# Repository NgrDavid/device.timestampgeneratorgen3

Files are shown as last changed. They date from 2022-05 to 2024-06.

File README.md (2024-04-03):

## Harp Timestamp Generator Gen3

This device generates programable timestamps to up to 6 harp devices.

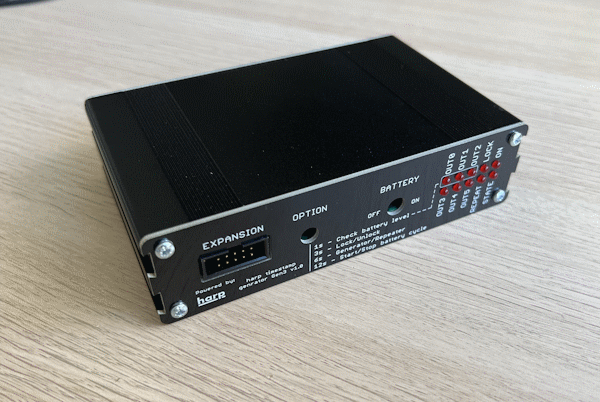
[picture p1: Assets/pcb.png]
HarpTimestampGeneratorGen3


### Key Features ###

* TBA

### Connectivity ###

* TBA

## Interface ##

The interface with the Harp Output Expander can be done through [Bonsai](https://bonsai-rx.org/).

## Licensing ##

Each subdirectory will contain a license or, possibly, a set of licenses if it involves both hardware and software.

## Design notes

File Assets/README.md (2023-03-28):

### Licensing
Copyright Filipe Carvalho 2021

<br />This work is licensed under a <a rel="license" href="http://creativecommons.org/licenses/by/4.0/">Creative Commons Attribution 4.0 International License</a>.

#### You are free to:
*Share* — copy and redistribute the material in any medium or format.

*Adapt* — remix, transform, and build upon the material for any purpose, even commercially.

#### Under the following terms:
*Attribution* — You must give appropriate credit, provide a link to the license, and indicate if changes were made. You may do so in any reasonable manner, but not in any way that suggests the licensor endorses you or your use.

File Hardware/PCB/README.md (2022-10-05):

# Harp Timestamp Generator Gen1

## Licensing

The designs, documentation, and photos available in this repository are free: you can redistribute it and/or modify it under the terms of the used license.
Check file named LICENSE.

Copyright OEPS 2021-2022

<br />This work is licensed under a <a rel="license" href="http://creativecommons.org/licenses/by-nc-sa/3.0/igo/">Creative Commons Attribution-NonCommercial-ShareAlike 3.0 IGO License</a>.

If your are interested in obtaining a license to sell this device, please contact info@oeps.tech

[1]: https://docs.google.com/spreadsheets/d/1aobmmEzBDethzIlrm1eg0eYkBqlyX3s9WbA9KgRwVQI/edit?usp=sharing

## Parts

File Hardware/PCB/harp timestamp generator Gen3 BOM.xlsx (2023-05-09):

Qty | Value | Package | Parts | MPN | Type
ASSEMBLY HOUSE
1 | CFPA | CFPA | BUTTON | CFPA-1FB4-A2T | SMD
30 | 100nF | C0402 | C1, C3, C5, C7, C9, C12, C13, C14, C15, C16, C17, C18, C19, C20, C21, C22, C25, C26, C27, C28, C30, C31, C32, C35, C36, C37, C38, C41, C42, C62 | CGA2B3X7R1H104K050BB | SMD
5 | 4.7uF | C0603 | C8, C10, C11, C23, C24 | C1608X6S1C475K080AC | SMD
1 | 4.7nF | C0402 | C2 | 885012205084 | SMD
1 | 330nF | C0402 | C29 | GRM155R61A334KE15D | SMD
2 | 10nF | C0402 | C33, C34 | GCM155R71E103KA37D | SMD
2 | 47pF | C0402 | C4, C6 | 04025A470JAT2A | SMD
1 | 100u 25V | TT2D6 | C39 | EEU-FM1E101B | TH
1 | 330pF | C0402 | C40 | C0402C331J5GAC7867 | SMD
7 | CLCK_JACK | 35RASMT2BHNTRX | CLKIN, CLKOUT0, CLKOUT1, CLKOUT2, CLKOUT3, CLKOUT4, CLKOUT5 | 35RASMT2BHNTRX | SMD
1 | 330 Ohms @ 100MHz | R0603 | F1 | BLM18SG331TN1D | SMD
2 | DNI | DNI | D1, D2 | DNI | DNI
1 | MCP73831T-2ATI/OT | TSOT23-5 | IC1 | MCP73831T-2ATI/OT | SMD
3 | SN74LVC1G125DBVT | SOT23-5 | IC10, IC18, IC19 | SN74LVC1G125DBVT | SMD
6 | SI8621BC-B-IS | SOIC8 | IC12, IC13, IC14, IC15, IC16, IC17 | SI8621BC-B-ISR | SMD | Replacements: SI8621BB-B-IS
1 | USBLC6-2SC6 | SOT23-6L | IC2 | USBLC6-2SC6 | SMD
1 | FT232RL | SSOP28 | IC3 | FT232RL-REEL | SMD
1 | TPS2114 | TSSOP8 | IC4 | TPS2114APWR | SMD
2 | TLV70033DDCR | TSOT23-5 | IC5, IC11 | LP5951MFX-3.3/NOPB | SMD
1 | ATXMEGA16A4U-AU | QFP80P1200X1200X120-44N | IC6 | ATXMEGA16A4U-A | SMD
3 | M74VHC1GT126DF1G | SC70-5 | IC7, IC8, IC9 | M74VHC1GT126DF1G | SMD
1 | 40R@100MHz | R0805 | L1 | MI0805K400R-10 | SMD
5 | 569-0112-100 | 569-011X-X00_LED_ARRAY | LED1, LED2, LED3, LED4, LED5 | 569-0111-100F | TH
1 | OSCILLATOR | OSCILLATOR_3.2X2.5 | OSC1 | O 32,0-JT32C-A-K-3,3-LF | SMD
1 | 2x3_header | MA03-2 | PDI | 67996-206HLF | TH
1 | RTU002P02T106 | SOT323 | Q1 | RTU002P02T106 | SMD
1 | BC817-40W | SOT323-BEC | Q2 | BC817-40W,135 | SMD
1 | BC817-40LT1SMD | SOT23-BEC | Q3 | SBC817-40LT1G | SMD
1 | DMG1012UW | SOT323 | Q4 | DMG1012UW-7 | SMD
1 | DMP2035U-7 | SOT323 | Q5 | PMF170XP,115 | SMD
1 | 1M | R0402 | R1 | CRCW04021M00FKED | SMD
3 | 100R | R0603 | R10, R11, R12 | CRCW0603100RFKEAHP | SMD
3 | 4k5 | R0402 | R13, R17, R19 | RT0402BRD074K53L | SMD
1 | 20R | R2512 | R15 | CRM2512-FX-20R0ELF | SMD
1 | 10R | R0402 | R2 | ERJ-PA2J100X | SMD
1 | 0R | R0402 | R20 | RC0402JR-070RL | SMD
1 | DNI | R0402 | R26 | DNI | DNI
12 | 1k | R0402 | R14, R21, R22, R23, R24, R25, R27, R28, R29, R30, R31, R_I_MAX | CRCW04021K00FKED | SMD
8 | 10k | R0402 | R3, R7, R9, R16, R18, R50, R54, R55 | CRCW040210K0FKED | SMD
10 | 330R | R0402 | R33, R34, R35, R36, R37, R40, R41, R42, R44, R45 | RC0402FR-07330RL | SMD
1 | 51k 0.1% | R0402 | R4 | ERA-2AEB513X | SMD
2 | 14k7 0.1% | R0402 | R5, R6 | RT0402BRD0714K7L | SMD
1 | 100k | R0402 | R48 | ERJ-2RKF1003X | SMD
1 | I/O Header | ML10L | SV1 | SBH11-PBPC-D05-RA-BK | TH
10 | BC850 | SOT23 | T1, T2, T3, T4, T5, T6, T7, T8, T9, T10 | BC850C,215 | SMD
1 | mini USB | 240-0002-1 | USB | UX60-MB-5S8 | SMD
1 | Switch SPDT | 7101MD9ABE | BATEN | 7101MD9ABE | TH
1 | B2B-PH-K-S(LF)(SN) | JST-XH-02-PACKAGE-ROUND-PAD | X1 | B2B-XH-A(LF)(SN) | TH
POST-PRODUCTION
1 |  |  | Front Panel PCB | PCBWAY
1 |  |  | Rear Panel PCB | PCBWAY
1 |  |  | Enclosure | B5-080BK
1 |  |  | Battery lithium Polymer 2 Ah | MIKROE-1120 | -
4 |  |  | Bumper Cylindrical Dome 9.53mm | SJ-5306-CLEAR-3000/CASE
ACCESSORIES
3 |  |  | 3.5mm stereo jack cable 0.3 m, Black | P312-001 | -
4 |  |  | 3.5mm stereo jack cable 1.2 m, Black | AV13646
1 |  |  | 0.9 left angle USB cable | USB2HABM3RA
NOTES
 |  |  |  | Number of unique parts | 48
 |  |  |  | Number of SMD unique parts | 42
 |  |  |  | Number of SMD parts | 135
 |  |  |  | Number of TH unique parts | 6
 |  |  |  | Number of TH parts | 10

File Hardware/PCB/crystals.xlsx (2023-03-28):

Digikey PN | MNF PN | @25C [ppm] | Range of temperatures [ppm] | Supply Change [ppm] | Load Change [ppm] | Aging/year [ppm] |  | Dimensions [mm] | Pinout | Current [mA] | Type
XC2259CT-ND | ECS-TXO-2520-33-320-AN-TR | 2 | 2.5 | 0.2 | 0.2 | 1 | 5.9 | 2.5 x 2.0 | En/Dis, GND, OUT, VDD | 6 | HCMOS TXCO
1908-1044-1-ND | O 32,0-JT32C-A-K-3,3-LF | 0.5 | 2.5 | 0.2 | 0.2 | 1 | 4.4 | 3.2 x 2.5 | En/Dis, GND, OUT, VDD | 4.8 | HCMOS TXCO
50-ECS-TXO-2520MV-320-AN-CT-ND | ECS-TXO-2520MV-320-AN-TR | 1.5 | 2.5 | 0.3 | 0.3 | 1 | 5.6 | 2.5 x 2.0 | En/Dis, GND, OUT, VDD | 6 | CMOS TXCO
50-ECS-TXO-2520MV-320-AY-CT-ND | ECS-TXO-2520MV-320-AY-TR | 1.5 | 2.5 | 0.3 | 0.3 | 1 | 5.6 | 2.5 x 2.0 | En/Dis, GND, OUT, VDD | 6 | CMOS TXCO
50-ECS-TXO-25CSMV-320-BM-CT-ND | ECS-TXO-25CSMV-320-BM-TR | 2 | 1 | 0.2 | 0.2 | 1 | 4.4 | 2.5 x 2.0 | GND, GND, OUT, VDD | 2.5 | Clipped Sinewave TSCO

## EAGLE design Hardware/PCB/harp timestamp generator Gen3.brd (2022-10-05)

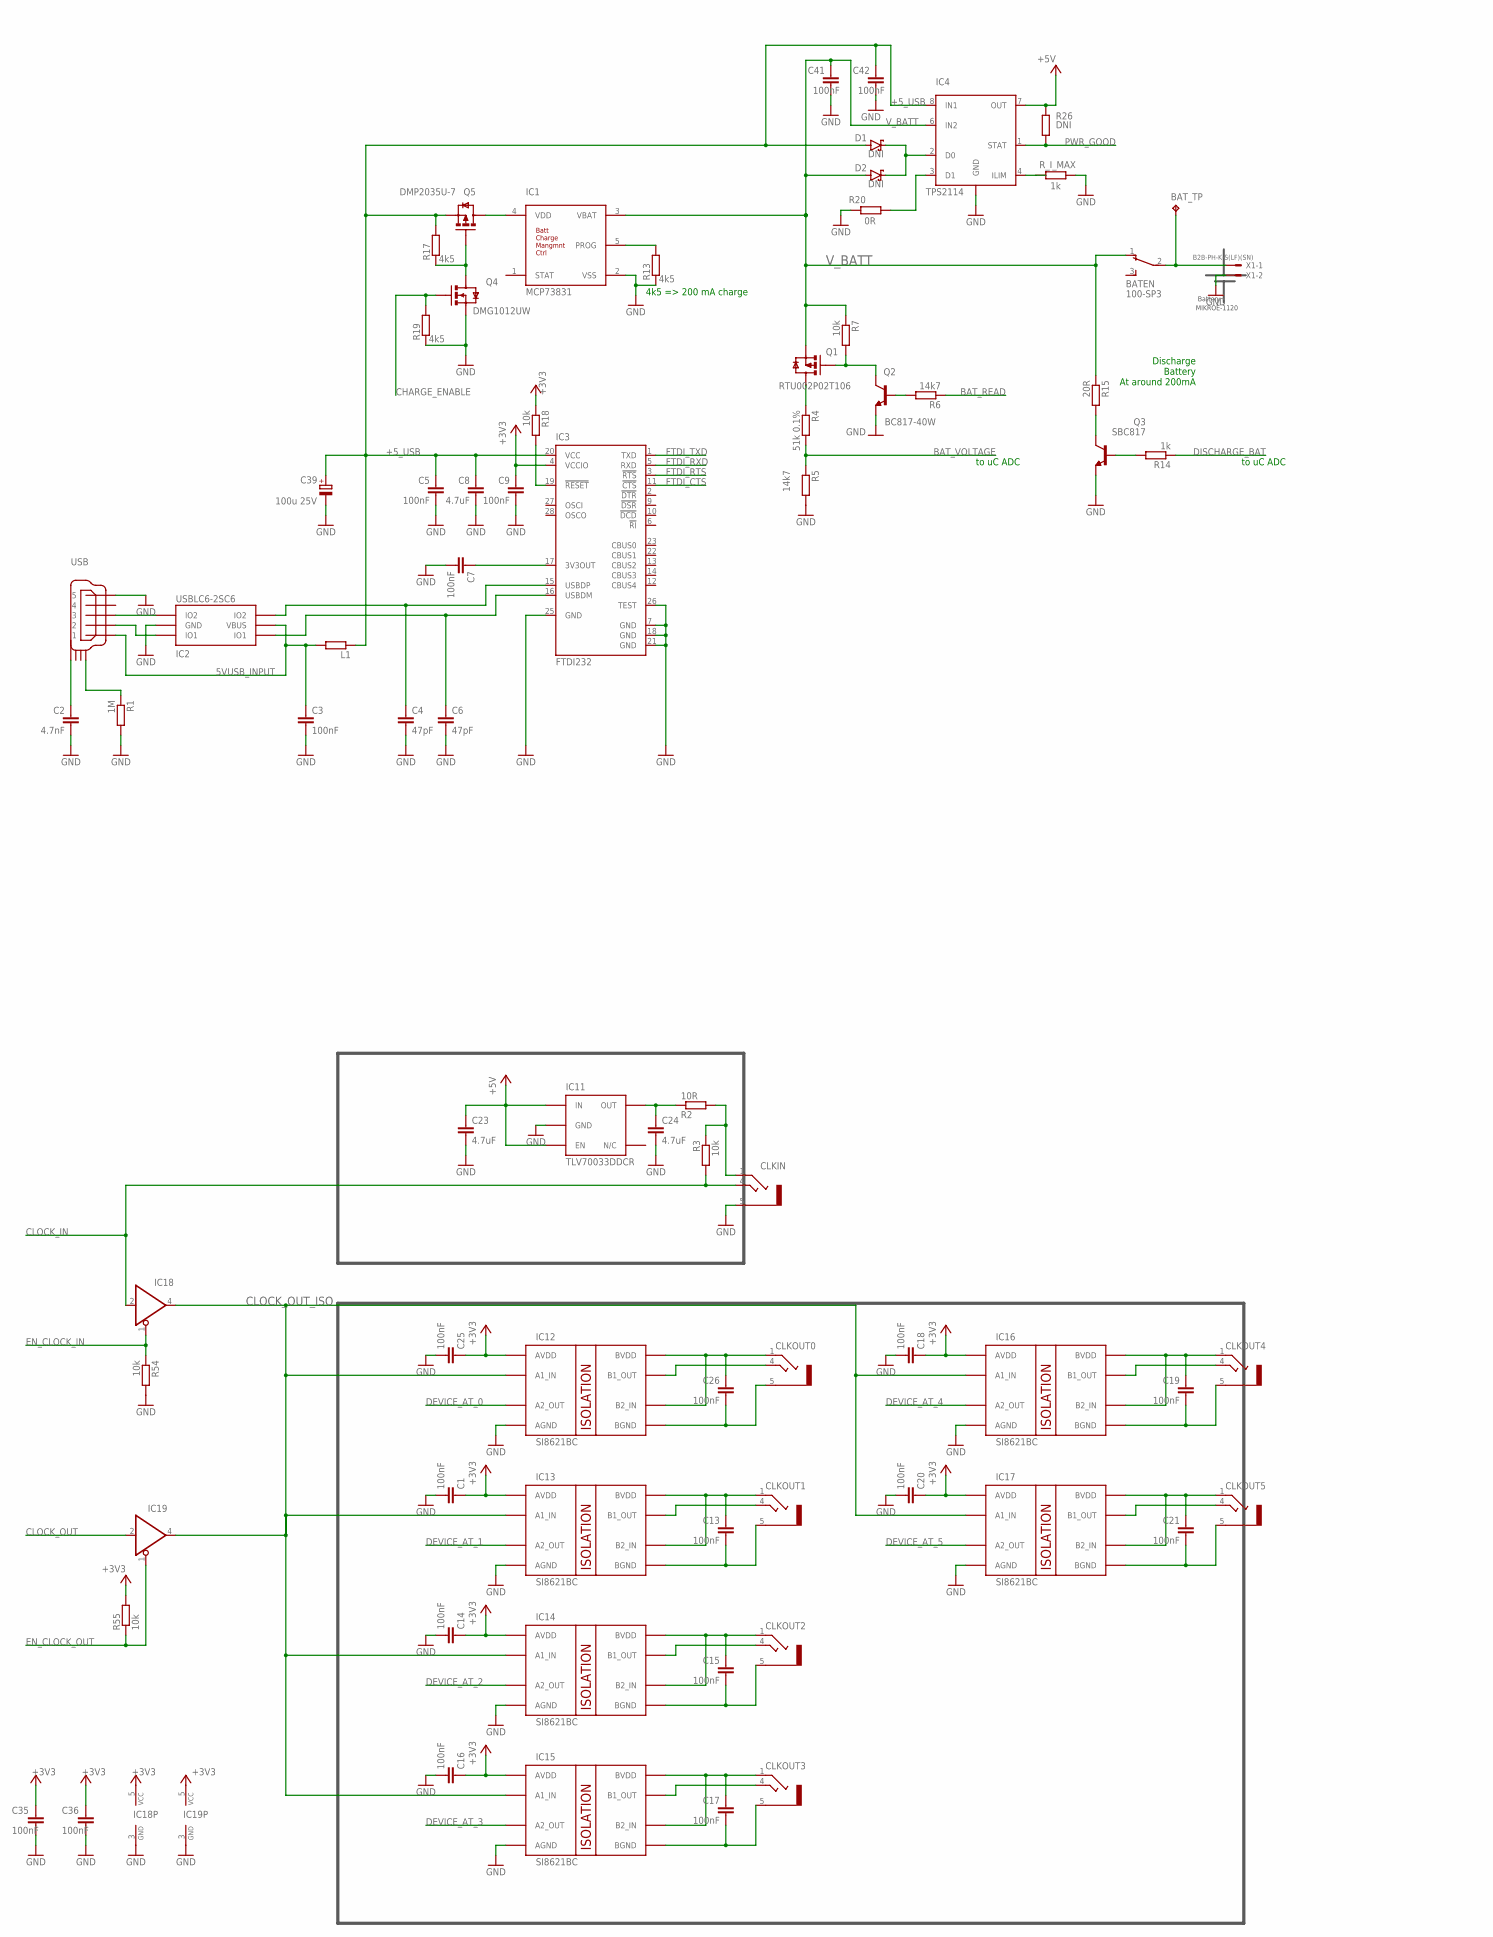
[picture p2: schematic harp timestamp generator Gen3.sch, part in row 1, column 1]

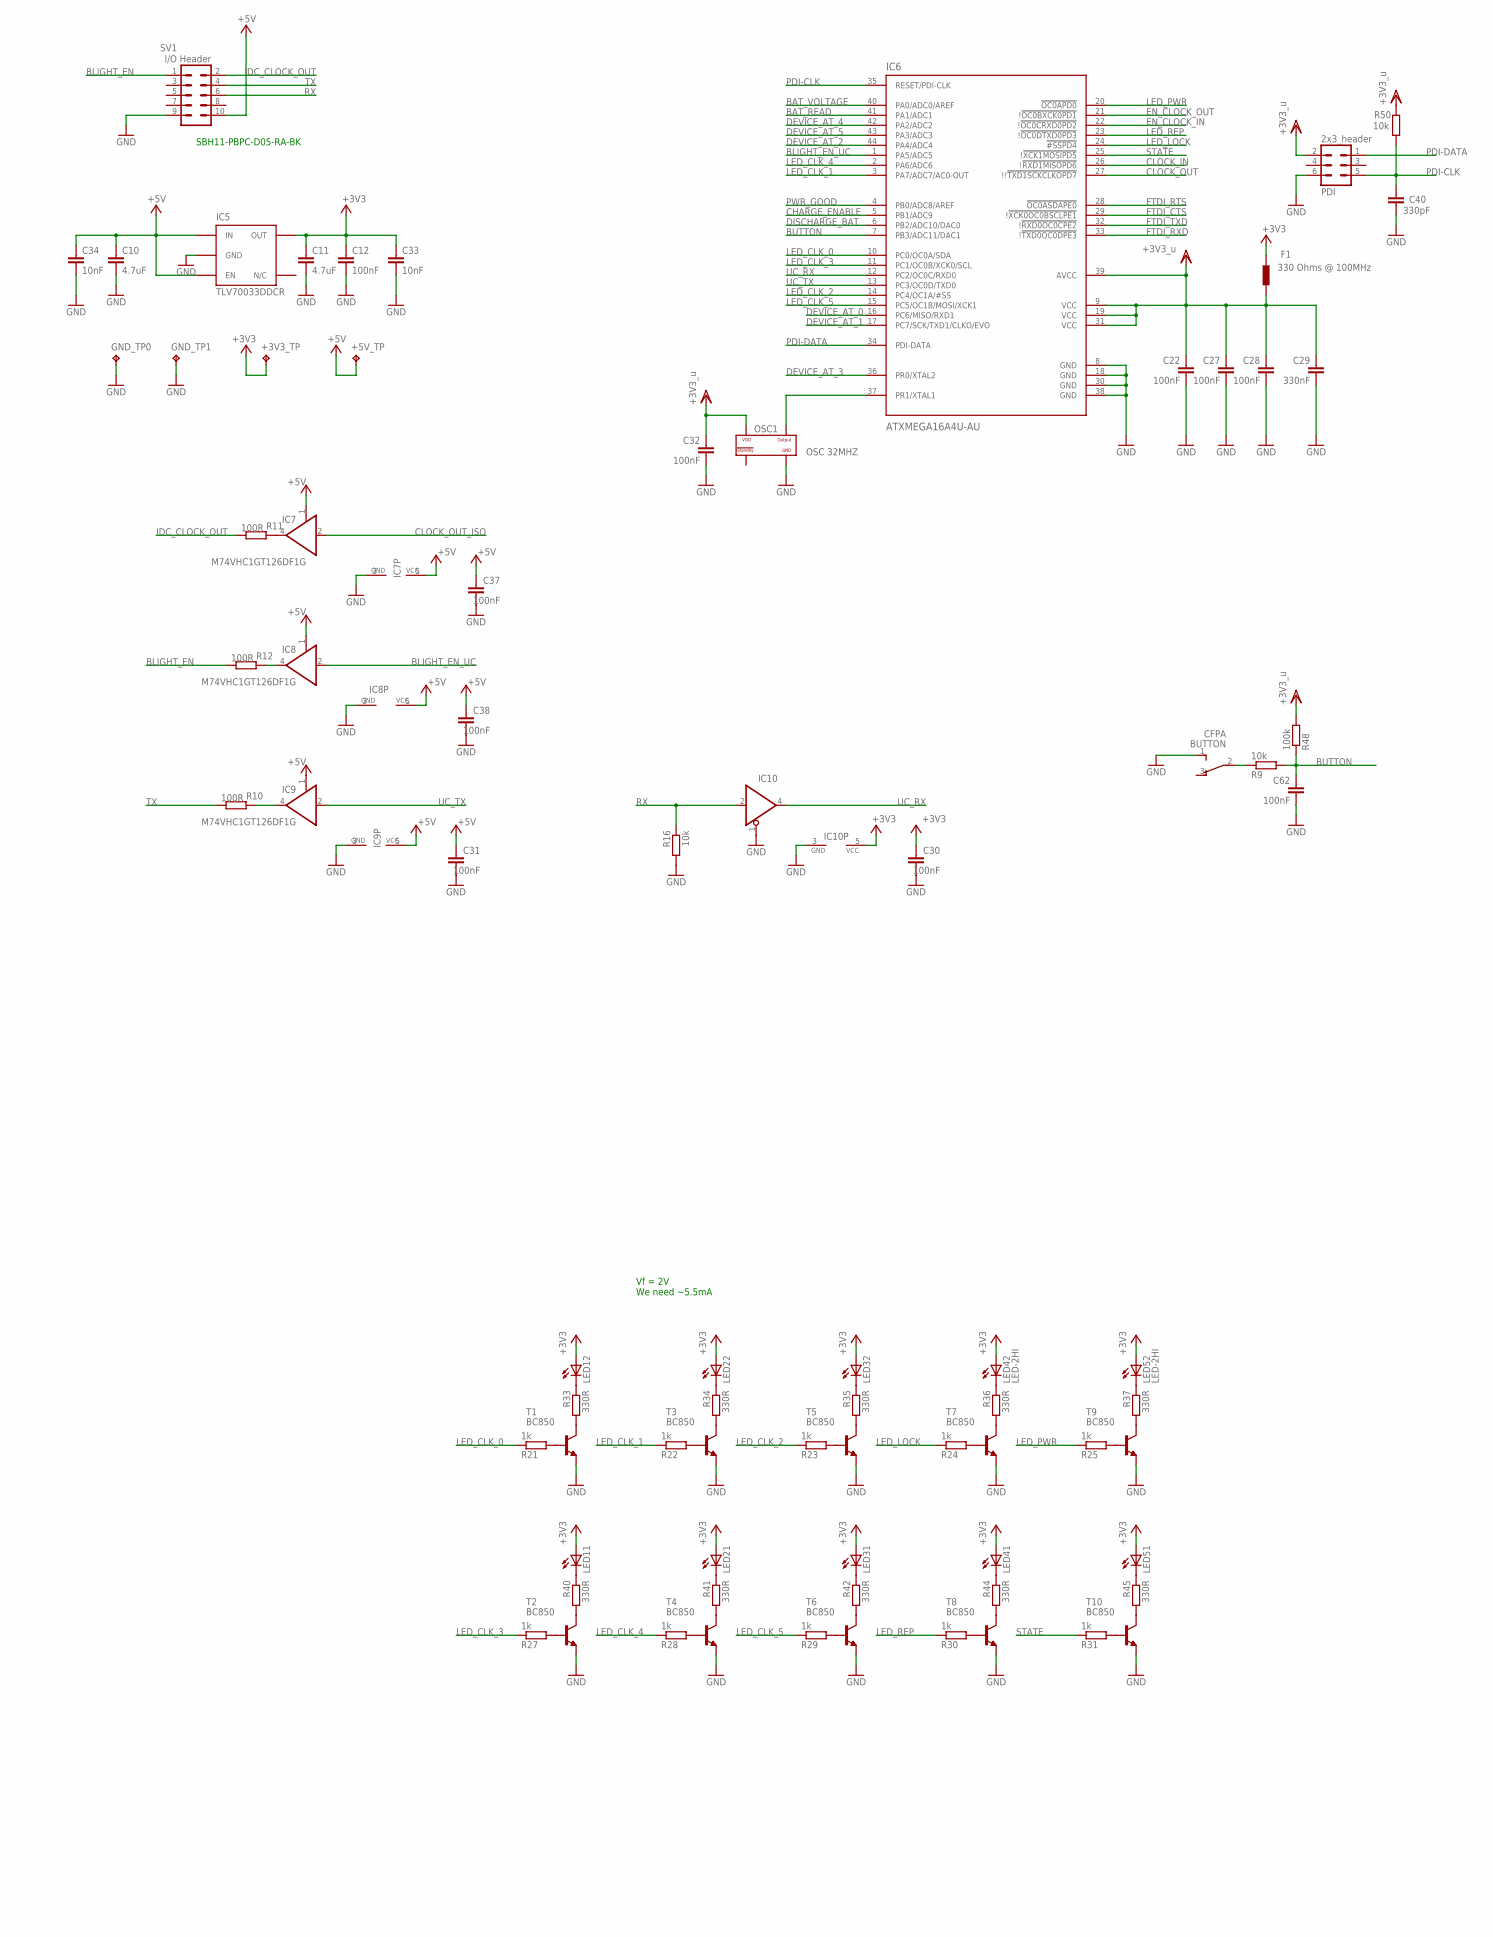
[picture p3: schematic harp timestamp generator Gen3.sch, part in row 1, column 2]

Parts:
+3V3_TP, +5V_TP: TPPAD1-13; P1-13; MPN n.a.
BATEN: 100-SP3; 2M1-SP1-T2-B4-M6RE; MPN 7101MD9ABE; DIGIKEY_PN CKN1045-ND Mouser: 611-7101-051
BAT_TP: TPPAD1-13; P1-13; MPN n.a.
BUTTON: CFPA; MPN CFPA-1FB4-A2T; DIGIKEY_PN 563-1246-1-ND
C1, C3, C5, C7, C9, C12, C13, C14, C15, C16, C17, C18, C19, C20, C21, C22, C25, C26, C27, C28, C30, C31, C32, C35, C36, C37, C38, C41, C42, C62: 100nF; C0402; MPN CGA2B3X7R1H104K050BB; DIGIKEY_PN 445-6899-2-ND
C2: 4.7nF; C0402; MPN UMK105B7472KV-F; DIGIKEY_PN 587-2237-1-ND
C4, C6: 47pF; C0402; MPN 04025A470JAT2A; DIGIKEY_PN 478-1078-1-ND
C8, C10, C11, C23, C24: 4.7uF; C0603; MPN EMK107ABJ475KA-T; DIGIKEY_PN 587-2786-1-ND
C29: 330nF; C0402; MPN GRM155R61A334KE15D; DIGIKEY_PN 490-3263-1-ND
C33, C34: 10nF; C0402; MPN CL05B103KB5NNNC; DIGIKEY_PN 1276-1028-1-ND
C39: 100u 25V; TT2D6; MPN EEUFM1E101B; DIGIKEY_PN P19702CT-ND
C40: 330pF; C0402; MPN C0402C331JAGAC7867; DIGIKEY_PN 399-11875-1-ND
CLKIN: CLCK_JACK; 35RASMT2BHNTRX; MPN 35RASMT2BHNTRX; DIGIKEY_PN SC1489-1-ND
CLKOUT0, CLKOUT1, CLKOUT2, CLKOUT3, CLKOUT4, CLKOUT5: CLCK_JACK; 35RASMT2BHNTRX; MPN 35RASMT2BHNTRX; DIGIKEY_PN SC1489-1-ND
D1, D2: DNI; SOD3715X135
F1: 330 Ohms @ 100MHz; R0603; MPN BLM18SG331TN1D; DIGIKEY_PN 490-3997-1-ND
GND_TP0, GND_TP1: TPPAD1-13; P1-13; MPN n.a.
IC1: MCP73831; TSOT23-5; DIGIKEY_PN MCP73831T-2ATI/OTCT-ND
IC2: USBLC6-2SC6; SOT23-6L; MPN USBLC6-2SC6; DIGIKEY_PN 497-5235-1-ND
IC3: FTDI232; SSOP28; MPN FT232RL-REEL; DIGIKEY_PN 768-1007-1-ND
IC4: TPS2114; TSSOP8; MPN TPS2114APWR; DIGIKEY_PN 296-16939-1-ND
IC5, IC11: TLV70033DDCR; TSOT23-5; MPN TLV70033DDCR; DIGIKEY_PN 296-27937-6-ND
IC6: ATXMEGA16A4U-AU; QFP80P1200X1200X120-44N; MPN ATXMEGA16A4U-AU; DIGIKEY_PN ATXMEGA16A4U-AU-ND
IC7, IC8, IC9: M74VHC1GT126DF1G; SC70-5; MPN M74VHC1GT126DF1G; DIGIKEY_PN M74VHC1GT126DF1GOSCT-ND
IC10, IC18, IC19: SN74LVC1G125DBVT; SOT23-5; MPN SN74LVC1G125DBVT; DIGIKEY_PN 296-26595-1-ND
IC12, IC13, IC14, IC15, IC16, IC17: SI8621BC; SOIC8; MPN Si8621BC-B-IS; DIGIKEY_PN 336-2064-5-ND
L1: 40R@100MHz; R0805; MPN MI0805K400R-10; DIGIKEY_PN 240-2389-1-ND
LED1, LED2, LED3, LED4, LED5: LED-2HI; 569-011X-X00_LED_ARRAY; MPN 5690111100F; DIGIKEY_PN 350-1782-ND
OSC1: OSC 32MHZ; OSCILLATOR_3.2X2.5; MPN O 32,0-JT32C-A-K-3,3-LF; DIGIKEY_PN 1908-1044-1-ND
PDI: 2x3_header; MA03-2; MPN 67996-206HLF; DIGIKEY_PN 609-3210-ND
Q1: RTU002P02T106; SOT323; MPN RTU002P02T106; DIGIKEY_PN RTU002P02T106CT-ND
Q2: BC817-40W; SOT323-BEC; MPN BC817-40W,135; DIGIKEY_PN 1727-6185-1-ND
Q3: SBC817; SOT23-BEC; MPN SBC817-40LT1G; DIGIKEY_PN SBC817-40LT1GOSCT-ND
Q4: DMG1012UW; SOT323; MPN DMG1012UW-7; DIGIKEY_PN DMG1012UW-7DICT-ND
Q5: DMP2035U-7; SOT323; DIGIKEY_PN DMP2035U-7DICT-ND
R1: 1M; R0402; MPN CRCW04021M00FKEDC; DIGIKEY_PN 541-3965-1-ND
R2: 10R; R0402; MPN CRCW040210R0FKEDHP; DIGIKEY_PN 541-10.0YCT-ND
R3, R7, R9, R16, R18, R50, R54, R55: 10k; R0402; MPN RMCF0402FT10K0; DIGIKEY_PN RMCF0402FT10K0CT-ND
R4: 51k 0.1%; R0402; MPN ERA-2AEB513X; DIGIKEY_PN P51KDCCT-ND
R5, R6: 14k7; R0402; MPN RT0402BRD0714K7L; DIGIKEY_PN YAG4174CT-ND
R10, R11, R12: 100R; R0603; MPN RT0603DRD07100RL; DIGIKEY_PN 311-100DCT-ND
R13, R17, R19: 4k5; R0402; MPN RT0402BRD074K53L; DIGIKEY_PN YAG1444CT-ND
R14, R21, R22, R23, R24, R25, R27, R28, R29, R30, R31: 1k; R0402; MPN RMCF0402FT1K00; DIGIKEY_PN RMCF0402FT1K00CT-ND
R15: 20R; R2512; MPN RCP2512W25R0GEB; DIGIKEY_PN 541-2662-1-ND
R20: 0R; R0402; MPN RMCF0402ZT0R00; DIGIKEY_PN RMCF0402ZT0R00CT-ND
R26: DNI; R0402; MPN DNI; DIGIKEY_PN DNI
R33, R34, R35, R36, R37, R40, R41, R42, R44, R45: 330R; R0402; MPN RC0402FR-07330RL; DIGIKEY_PN 311-330LRCT-ND
R48: 100k; R0402; MPN ERJ-2RHD1002X; DIGIKEY_PN P15984CT-ND
R_I_MAX: 1k; R0402; MPN RMCF0402FT1K00; DIGIKEY_PN RMCF0402FT1K00CT-ND Mouser ERJ-2RKF1001X
SV1: I/O Header; ML10L; MPN SBH11-PBPC-D05-RA-BK; DIGIKEY_PN S9177-ND
T1, T2, T3, T4, T5, T6, T7, T8, T9, T10: BC850; SOT23; MPN BC850C,215; DIGIKEY_PN 1727-4862-1-ND
USB: mini USB; 240-0002-1; MPN UX60-MB-5S8; DIGIKEY_PN H2960TR-ND
X1: B2B-PH-K-S(LF)(SN); JST-XH-02-PACKAGE-ROUND-PAD; MPN B2B-PH-K-S(LF)(SN); DIGIKEY_PN 455-1704-ND

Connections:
5VUSB_INPUT: C3.1, IC2.P$5 (VBUS), L1.2, USB.P$1 (1)
+3V3: +3V3_TP.TP, C1.1, C9.1, C11.1, C12.1, C14.1, C16.1, C18.1, C20.1, C25.1, C30.1, C33.1, C35.1, C36.1, F1.2, IC3.4 (VCCIO), IC5.5 (OUT), IC10.5 (VCC), IC12.1 (AVDD), IC13.1 (AVDD), IC14.1 (AVDD), IC15.1 (AVDD), IC16.1 (AVDD), IC17.1 (AVDD), IC18.5 (VCC), IC19.5 (VCC), LED1.A1 (A), LED1.A2 (A), LED2.A1 (A), LED2.A2 (A), LED3.A1 (A), LED3.A2 (A), LED4.A1 (A), LED4.A2 (A), LED5.A1 (A), LED5.A2 (A), R18.1, R55.2
+5V: +5V_TP.TP, C10.1, C23.1, C31.1, C34.1, C37.1, C38.1, IC4.7 (OUT), IC5.1 (IN), IC5.3 (EN), IC7.1 (OE), IC7.5 (VCC), IC8.1 (OE), IC8.5 (VCC), IC9.1 (OE), IC9.5 (VCC), IC11.1 (IN), IC11.3 (EN), R26.1, SV1.10
+5_USB: C5.1, C8.1, C39.+, C42.1, D1.2 (A), IC3.20 (VCC), IC4.8 (IN1), L1.1, Q5.1 (S), R17.2
BAT_READ: IC6.41 (PA1/ADC1), R6.1
BAT_VOLTAGE: IC6.40 (PA0/ADC0/AREF), R4.2, R5.1
BLIGHT_EN: R12.1, SV1.1
BLIGHT_EN_UC: IC6.1 (PA5/ADC5), IC8.2 (I)
BUTTON: C62.1, IC6.7 (PB3/ADC11/DAC1), R9.2, R48.1
CHARGE_ENABLE: IC6.5 (PB1/ADC9), Q4.2 (G), R19.2
CLKOUT0: CLKOUT0.4, IC12.7 (B1_OUT)
CLKOUT1: CLKOUT1.4, IC13.7 (B1_OUT)
CLKOUT2: CLKOUT2.4, IC14.7 (B1_OUT)
CLKOUT3: CLKOUT3.4, IC15.7 (B1_OUT)
CLKOUT4: CLKOUT4.4, IC16.7 (B1_OUT)
CLKOUT5: CLKOUT5.4, IC17.7 (B1_OUT)
CLOCK_IN: CLKIN.4, IC6.26 (!!RXD1MISOPD6), IC18.2 (I), R3.2
CLOCK_OUT: IC6.27 (!!!TXD1SCKCLKOPD7), IC19.2 (I)
CLOCK_OUT_ISO: IC7.2 (I), IC12.2 (A1_IN), IC13.2 (A1_IN), IC14.2 (A1_IN), IC15.2 (A1_IN), IC16.2 (A1_IN), IC17.2 (A1_IN), IC18.4 (O), IC19.4 (O)
DEVICE_AT_0: IC6.16 (PC6/MISO/RXD1), IC12.3 (A2_OUT)
DEVICE_AT_1: IC6.17 (PC7/SCK/TXD1/CLKO/EVO), IC13.3 (A2_OUT)
DEVICE_AT_2: IC6.44 (PA4/ADC4), IC14.3 (A2_OUT)
DEVICE_AT_3: IC6.36 (PR0/XTAL2), IC15.3 (A2_OUT)
DEVICE_AT_4: IC6.42 (PA2/ADC2), IC16.3 (A2_OUT)
DEVICE_AT_5: IC6.43 (PA3/ADC3), IC17.3 (A2_OUT)
DISCHARGE_BAT: IC6.6 (PB2/ADC10/DAC0), R14.1
EN_CLOCK_IN: IC6.22 (!!OC0CRXD0PD2), IC18.1 (OE), R54.1
EN_CLOCK_OUT: IC6.21 (!!OC0BXCK0PD1), IC19.1 (OE), R55.1
FTDI_CTS: IC3.11 (!CTS), IC6.29 (!!XCK0OC0BSCLPE1)
FTDI_RTS: IC3.3 (!RTS), IC6.28 (!OC0ASDAPE0)
FTDI_RXD: IC3.5 (RXD), IC6.33 (!!TXD0OC0DPE3)
FTDI_TXD: IC3.1 (TXD), IC6.32 (!!RXD0OC0CPE2)
GND: BUTTON.1 (3), C1.2, C2.2, C3.2, C4.2, C5.2, C6.2, C7.2, C8.2, C9.2, C10.2, C11.2, C12.2, C14.2, C16.2, C18.2, C20.2, C22.2, C23.2, C24.2, C25.2, C27.2, C28.2, C29.2, C30.2, C31.2, C32.2, C33.2, C34.2, C35.2, C36.2, C37.2, C38.2, C39.-, C40.2, C41.2, C42.2, C62.2, CLKIN.5, GND_TP0.TP, GND_TP1.TP, IC1.2 (VSS), IC2.P$2 (GND), IC3.7 (GND), IC3.18 (GND), IC3.21 (GND), IC3.25 (GND), IC3.26 (TEST), IC4.5 (GND), IC5.2 (GND), IC6.8 (GND), IC6.18 (GND), IC6.30 (GND), IC6.38 (GND), IC7.3 (GND), IC8.3 (GND), IC9.3 (GND), IC10.1 (OE), IC10.3 (GND), IC11.2 (GND), IC12.4 (AGND), IC13.4 (AGND), IC14.4 (AGND), IC15.4 (AGND), IC16.4 (AGND), IC17.4 (AGND), IC18.3 (GND), IC19.3 (GND), OSC1.P$2 (GND), PDI.6, Q2.E, Q3.E, Q4.1 (S), R1.2, R5.2, R13.1, R16.2, R19.1, R20.1, R54.2, R_I_MAX.2, SV1.9, T1.2 (E), T2.2 (E), T3.2 (E), T4.2 (E), T5.2 (E), T6.2 (E), T7.2 (E), T8.2 (E), T9.2 (E), T10.2 (E), USB.P$5 (5), X1.2
GND_ISO: C26.2, CLKOUT0.5, IC12.5 (BGND)
GND_ISO1: C13.2, CLKOUT1.5, IC13.5 (BGND)
GND_ISO2: C15.2, CLKOUT2.5, IC14.5 (BGND)
GND_ISO3: C17.2, CLKOUT3.5, IC15.5 (BGND)
GND_ISO4: C19.2, CLKOUT4.5, IC16.5 (BGND)
GND_ISO5: C21.2, CLKOUT5.5, IC17.5 (BGND)
IDC_CLOCK_OUT: R11.1, SV1.2
LED_CLK_0: IC6.10 (PC0/OC0A/SDA), R21.1
LED_CLK_1: IC6.3 (PA7/ADC7/AC0-OUT), R22.1
LED_CLK_2: IC6.14 (PC4/OC1A/#SS), R23.1
LED_CLK_3: IC6.11 (PC1/OC0B/XCK0/SCL), R27.1
LED_CLK_4: IC6.2 (PA6/ADC6), R28.1
LED_CLK_5: IC6.15 (PC5/OC1B/MOSI/XCK1), R29.1
LED_LOCK: IC6.24 (!#SSPD4), R24.1
LED_PWR: IC6.20 (!OC0APD0), R25.1
LED_REP: IC6.23 (!!OC0DTXD0PD3), R30.1
unnamed: R24.2, T7.1 (B)
unnamed: Q4.3 (D), Q5.2 (G), R17.1
unnamed: IC8.4 (O), R12.2
unnamed: IC9.4 (O), R10.2
unnamed: C26.1, CLKOUT0.1, IC12.6 (B2_IN), IC12.8 (BVDD)
unnamed: C13.1, CLKOUT1.1, IC13.6 (B2_IN), IC13.8 (BVDD)
unnamed: R36.2, T7.3 (C)
unnamed: IC7.4 (O), R11.2
unnamed: IC1.4 (VDD), Q5.3 (D)
unnamed: C15.1, CLKOUT2.1, IC14.6 (B2_IN), IC14.8 (BVDD)
unnamed: R22.2, T3.1 (B)
unnamed: IC1.5 (PROG), R13.2
unnamed: R21.2, T1.1 (B)
unnamed: LED3.C1 (C), R42.1
unnamed: R33.2, T1.3 (C)
unnamed: R27.2, T2.1 (B)
unnamed: R34.2, T3.3 (C)
unnamed: R40.2, T2.3 (C)
unnamed: LED3.C2 (C), R35.1
unnamed: R28.2, T4.1 (B)
unnamed: R41.2, T4.3 (C)
unnamed: R23.2, T5.1 (B)
unnamed: R35.2, T5.3 (C)
unnamed: R29.2, T6.1 (B)
unnamed: R42.2, T6.3 (C)
unnamed: LED1.C2 (C), R33.1
unnamed: LED2.C2 (C), R34.1
unnamed: LED1.C1 (C), R40.1
unnamed: LED2.C1 (C), R41.1
unnamed: R30.2, T8.1 (B)
unnamed: Q3.B, R14.2
unnamed: Q3.C, R15.2
unnamed: C17.1, CLKOUT3.1, IC15.6 (B2_IN), IC15.8 (BVDD)
unnamed: C7.1, IC3.17 (3V3OUT)
unnamed: IC2.P$1 (IO1), USB.P$2 (2)
unnamed: CLKIN.1, R2.2, R3.1
unnamed: C24.1, IC11.5 (OUT), R2.1
unnamed: BUTTON.2, R9.1
unnamed: C19.1, CLKOUT4.1, IC16.6 (B2_IN), IC16.8 (BVDD)
unnamed: R44.2, T8.3 (C)
unnamed: C21.1, CLKOUT5.1, IC17.6 (B2_IN), IC17.8 (BVDD)
unnamed: IC2.P$3 (IO2), USB.P$3 (3)
unnamed: R25.2, T9.1 (B)
unnamed: R37.2, T9.3 (C)
unnamed: R31.2, T10.1 (B)
unnamed: C2.1, USB.SHIELD_4
unnamed: R45.2, T10.3 (C)
unnamed: R1.1, USB.SHIELD_1
unnamed: LED5.C1 (C), R45.1
unnamed: LED5.C2 (C), R37.1
unnamed: LED4.C2 (C), R36.1
unnamed: LED4.C1 (C), R44.1
unnamed: BATEN.2, BAT_TP.TP, X1.1
unnamed: Q1.3 (D), R4.1
unnamed: IC4.4 (ILIM), R_I_MAX.1
unnamed: Q1.2 (G), Q2.C, R7.2
unnamed: Q2.B, R6.2
unnamed: D1.1 (C), D2.1 (C), IC4.2 (D0)
unnamed: IC4.3 (D1), R20.2
unnamed: IC3.19 (!RESET), R18.2
OSC1: IC6.37 (PR1/XTAL1), OSC1.P$3 (OUTPUT)
PDI-CLK: C40.1, IC6.35 (RESET/PDI-CLK), PDI.5, R50.1
PDI-DATA: IC6.34 (PDI-DATA), PDI.1
PWR_GOOD: IC4.1 (STAT), IC6.4 (PB0/ADC8/AREF), R26.2
RX: IC10.2 (I), R16.1, SV1.6
STATE: IC6.25 (!!XCK1MOSIPD5), R31.1
TX: R10.1, SV1.4
UC_RX: IC6.12 (PC2/OC0C/RXD0), IC10.4 (O)
UC_TX: IC6.13 (PC3/OC0D/TXD0), IC9.2 (I)
USBDM: C6.1, IC2.P$6 (IO1), IC3.16 (USBDM)
USBDP: C4.1, IC2.P$4 (IO2), IC3.15 (USBDP)
VDD: C22.1, C27.1, C28.1, C29.1, C32.1, F1.1, IC6.9 (VCC), IC6.19 (VCC), IC6.31 (VCC), IC6.39 (AVCC), OSC1.P$4 (VDD), PDI.2, R48.2, R50.2
V_BATT: BATEN.1, C41.1, D2.2 (A), IC1.3 (VBAT), IC4.6 (IN2), Q1.1 (S), R7.1, R15.1

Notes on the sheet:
Vf = 2V We need ~5.5mA
SBH11-PBPC-D05-RA-BK
4k5 => 200 mA charge
Battery
to uC ADC
MIKROE-1120
Discharge Battery At around 200mA

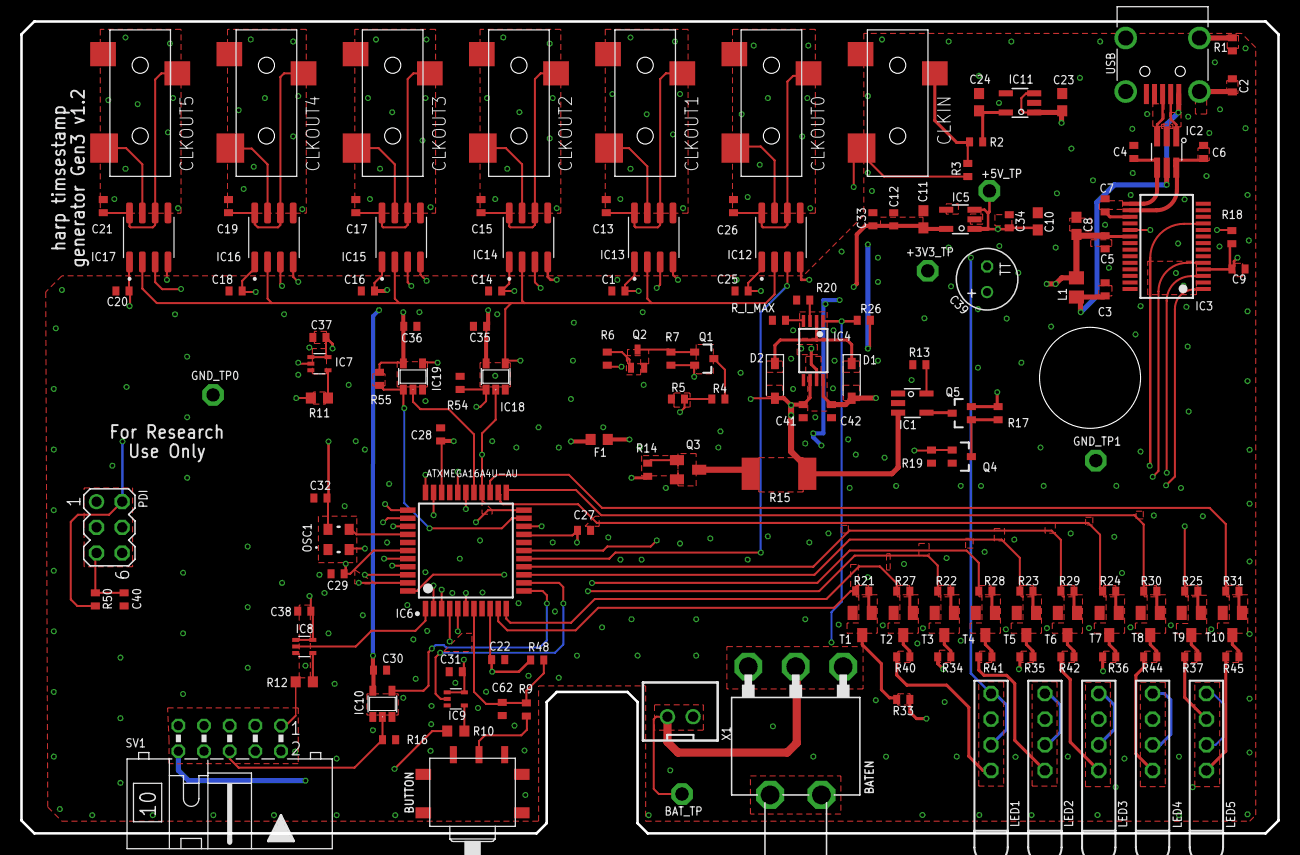
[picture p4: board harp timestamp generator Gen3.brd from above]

Board: 4 copper layers, 124.5 x 80.4 mm, 150 parts (0 on the bottom side), 122 nets.

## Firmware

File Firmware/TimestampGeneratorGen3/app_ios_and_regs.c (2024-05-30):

#include <avr/io.h>
#include "hwbp_core_types.h"
#include "app_ios_and_regs.h"

/************************************************************************/
/* Configure and initialize IOs                                         */
/************************************************************************/
void init_ios(void)
{	/* Configure input pins */
	io_pin2in(&PORTA, 2, PULL_IO_TRISTATE, SENSE_IO_NO_INT_USED);        // DEVICE_AT_4
	io_pin2in(&PORTA, 3, PULL_IO_TRISTATE, SENSE_IO_NO_INT_USED);        // DEVICE_AT_5
	io_pin2in(&PORTA, 4, PULL_IO_TRISTATE, SENSE_IO_NO_INT_USED);        // DEVICE_AT_2
	io_pin2in(&PORTB, 0, PULL_IO_UP, SENSE_IO_EDGES_BOTH);               // POWER_GOOD
	io_pin2in(&PORTB, 3, PULL_IO_TRISTATE, SENSE_IO_EDGES_BOTH);         // BUTTON
	io_pin2in(&PORTC, 6, PULL_IO_TRISTATE, SENSE_IO_NO_INT_USED);        // DEVICE_AT_0
	io_pin2in(&PORTC, 7, PULL_IO_TRISTATE, SENSE_IO_NO_INT_USED);        // DEVICE_AT_1
	io_pin2in(&PORTR, 0, PULL_IO_TRISTATE, SENSE_IO_NO_INT_USED);        // DEVICE_AT_3

	/* Configure input interrupts */
	io_set_int(&PORTB, INT_LEVEL_LOW, 0, (1<<0), false);                 // POWER_GOOD

	/* Configure output pins */
	io_pin2out(&PORTA, 1, OUT_IO_DIGITAL, IN_EN_IO_EN);                  // BAT_READ
	io_pin2out(&PORTA, 5, OUT_IO_DIGITAL, IN_EN_IO_EN);                  // EN_SCREEN_BACKLIGHT
	io_pin2out(&PORTA, 6, OUT_IO_DIGITAL, IN_EN_IO_EN);                  // LED_CLK_4
	io_pin2out(&PORTA, 7, OUT_IO_DIGITAL, IN_EN_IO_EN);                  // LED_CLK_1
	io_pin2out(&PORTB, 1, OUT_IO_DIGITAL, IN_EN_IO_EN);                  // EN_CHARGE
	io_pin2out(&PORTB, 2, OUT_IO_DIGITAL, IN_EN_IO_EN);                  // EN_DISCHARGE
	io_pin2out(&PORTC, 0, OUT_IO_DIGITAL, IN_EN_IO_EN);                  // LED_CLK_0
	io_pin2out(&PORTC, 1, OUT_IO_DIGITAL, IN_EN_IO_EN);                  // LED_CLK_3
	io_pin2out(&PORTC, 4, OUT_IO_DIGITAL, IN_EN_IO_EN);                  // LED_CLK_2
	io_pin2out(&PORTC, 5, OUT_IO_DIGITAL, IN_EN_IO_EN);                  // LED_CLK_5
	io_pin2out(&PORTD, 0, OUT_IO_DIGITAL, IN_EN_IO_EN);                  // LED_POWER
	io_pin2out(&PORTD, 1, OUT_IO_DIGITAL, IN_EN_IO_EN);                  // EN_CLOCK_OUT
	io_pin2out(&PORTD, 2, OUT_IO_DIGITAL, IN_EN_IO_EN);                  // EN_CLOCK_IN
	io_pin2out(&PORTD, 3, OUT_IO_DIGITAL, IN_EN_IO_EN);                  // LED_REPEATER
	io_pin2out(&PORTD, 4, OUT_IO_DIGITAL, IN_EN_IO_EN);                  // LED_LOCK
	io_pin2out(&PORTD, 5, OUT_IO_DIGITAL, IN_EN_IO_EN);                  // LED_STATE

	/* Initialize output pins */
	clr_BAT_READ;
	clr_EN_SCREEN_BACKLIGHT;
	clr_LED_CLK_4;
	clr_LED_CLK_1;
	clr_EN_CHARGE;
	clr_EN_DISCHARGE;
	clr_LED_CLK_0;
	clr_LED_CLK_3;
	clr_LED_CLK_2;
	clr_LED_CLK_5;
	clr_LED_POWER;
	clr_EN_CLOCK_OUT;
	set_EN_CLOCK_IN;
	clr_LED_REPEATER;
	clr_LED_LOCK;
	clr_LED_STATE;
}

/************************************************************************/
/* Registers' stuff                                                     */
/************************************************************************/
AppRegs app_regs;

uint8_t app_regs_type[] = {
	TYPE_U8,
	TYPE_U8,
	TYPE_U8,
	TYPE_U8,
	TYPE_FLOAT,
	TYPE_FLOAT,
	TYPE_FLOAT,
	TYPE_U16,
	TYPE_U16,
	TYPE_U32,
	TYPE_U8
};

uint16_t app_regs_n_elements[] = {
	1,
	1,
	1,
	1,
	1,
	1,
	1,
	1,
	1,
	1,
	1
};

uint8_t *app_regs_pointer[] = {
	(uint8_t*)(&app_regs.REG_CONFIG),
	(uint8_t*)(&app_regs.REG_DEVICES_CONNECTED),
	(uint8_t*)(&app_regs.REG_REPEATER_STATUS),
	(uint8_t*)(&app_regs.REG_BATTERY_RATE),
	(uint8_t*)(&app_regs.REG_BATTERY),
	(uint8_t*)(&app_regs.REG_BATTERY_TH_LOW),
	(uint8_t*)(&app_regs.REG_BATTERY_TH_HIGH),
	(uint8_t*)(&app_regs.REG_BATTERY_CALIBRATION0),
	(uint8_t*)(&app_regs.REG_BATTERY_CALIBRATION1),
	(uint8_t*)(&app_regs.REG_TIMER),
	(uint8_t*)(&app_regs.REG_TIMER_FREQUENCY)
};

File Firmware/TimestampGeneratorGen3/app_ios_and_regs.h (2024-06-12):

#ifndef _APP_IOS_AND_REGS_H_
#define _APP_IOS_AND_REGS_H_
#include "cpu.h"

void init_ios(void);
/************************************************************************/
/* Definition of input pins                                             */
/************************************************************************/
// DEVICE_AT_4            Description: Device is connected to CLKOUT4
// DEVICE_AT_5            Description: Device is connected to CLKOUT5
// DEVICE_AT_2            Description: Device is connected to CLKOUT2
// POWER_GOOD             Description: Detects the presence of the USB power
// BUTTON                 Description: User's input button
// DEVICE_AT_0            Description: Device is connected to CLKOUT0
// DEVICE_AT_1            Description: Device is connected to CLKOUT1
// DEVICE_AT_3            Description: Device is connected to CLKOUT3

#define read_DEVICE_AT_4 read_io(PORTA, 2)      // DEVICE_AT_4
#define read_DEVICE_AT_5 read_io(PORTA, 3)      // DEVICE_AT_5
#define read_DEVICE_AT_2 read_io(PORTA, 4)      // DEVICE_AT_2
#define read_POWER_GOOD read_io(PORTB, 0)       // POWER_GOOD
#define read_BUTTON read_io(PORTB, 3)           // BUTTON
#define read_DEVICE_AT_0 read_io(PORTC, 6)      // DEVICE_AT_0
#define read_DEVICE_AT_1 read_io(PORTC, 7)      // DEVICE_AT_1
#define read_DEVICE_AT_3 read_io(PORTR, 0)      // DEVICE_AT_3

/************************************************************************/
/* Definition of output pins                                            */
/************************************************************************/
// BAT_READ               Description: 
// EN_SCREEN_BACKLIGHT    Description: 
// LED_CLK_4              Description: 
// LED_CLK_1              Description: 
// EN_CHARGE              Description: 
// EN_DISCHARGE           Description: 
// LED_CLK_0              Description: 
// LED_CLK_3              Description: 
// LED_CLK_2              Description: 
// LED_CLK_5              Description: 
// LED_POWER              Description: 
// EN_CLOCK_OUT           Description: 
// EN_CLOCK_IN            Description: 
// LED_REPEATER           Description: 
// LED_LOCK               Description: 
// LED_STATE              Description: 

/* BAT_READ */
#define set_BAT_READ set_io(PORTA, 1)
#define clr_BAT_READ clear_io(PORTA, 1)
#define tgl_BAT_READ toggle_io(PORTA, 1)
#define read_BAT_READ read_io(PORTA, 1)

/* EN_SCREEN_BACKLIGHT */
#define set_EN_SCREEN_BACKLIGHT set_io(PORTA, 5)
#define clr_EN_SCREEN_BACKLIGHT clear_io(PORTA, 5)
#define tgl_EN_SCREEN_BACKLIGHT toggle_io(PORTA, 5)
#define read_EN_SCREEN_BACKLIGHT read_io(PORTA, 5)

/* LED_CLK_4 */
#define set_LED_CLK_4 set_io(PORTA, 6)
#define clr_LED_CLK_4 clear_io(PORTA, 6)
#define tgl_LED_CLK_4 toggle_io(PORTA, 6)
#define read_LED_CLK_4 read_io(PORTA, 6)

/* LED_CLK_1 */
#define set_LED_CLK_1 set_io(PORTA, 7)
#define clr_LED_CLK_1 clear_io(PORTA, 7)
#define tgl_LED_CLK_1 toggle_io(PORTA, 7)
#define read_LED_CLK_1 read_io(PORTA, 7)

/* EN_CHARGE */
#define set_EN_CHARGE set_io(PORTB, 1)
#define clr_EN_CHARGE clear_io(PORTB, 1)
#define tgl_EN_CHARGE toggle_io(PORTB, 1)
#define read_EN_CHARGE read_io(PORTB, 1)

/* EN_DISCHARGE */
#define set_EN_DISCHARGE set_io(PORTB, 2)
#define clr_EN_DISCHARGE clear_io(PORTB, 2)
#define tgl_EN_DISCHARGE toggle_io(PORTB, 2)
#define read_EN_DISCHARGE read_io(PORTB, 2)

/* LED_CLK_0 */
#define set_LED_CLK_0 set_io(PORTC, 0)
#define clr_LED_CLK_0 clear_io(PORTC, 0)
#define tgl_LED_CLK_0 toggle_io(PORTC, 0)
#define read_LED_CLK_0 read_io(PORTC, 0)

/* LED_CLK_3 */
#define set_LED_CLK_3 set_io(PORTC, 1)
#define clr_LED_CLK_3 clear_io(PORTC, 1)
#define tgl_LED_CLK_3 toggle_io(PORTC, 1)
#define read_LED_CLK_3 read_io(PORTC, 1)

/* LED_CLK_2 */
#define set_LED_CLK_2 set_io(PORTC, 4)
#define clr_LED_CLK_2 clear_io(PORTC, 4)
#define tgl_LED_CLK_2 toggle_io(PORTC, 4)
#define read_LED_CLK_2 read_io(PORTC, 4)

/* LED_CLK_5 */
#define set_LED_CLK_5 set_io(PORTC, 5)
#define clr_LED_CLK_5 clear_io(PORTC, 5)
#define tgl_LED_CLK_5 toggle_io(PORTC, 5)
#define read_LED_CLK_5 read_io(PORTC, 5)

/* LED_POWER */
#define set_LED_POWER set_io(PORTD, 0)
#define clr_LED_POWER clear_io(PORTD, 0)
#define tgl_LED_POWER toggle_io(PORTD, 0)
#define read_LED_POWER read_io(PORTD, 0)

/* EN_CLOCK_OUT */
#define set_EN_CLOCK_OUT clear_io(PORTD, 1)
#define clr_EN_CLOCK_OUT set_io(PORTD, 1)
#define tgl_EN_CLOCK_OUT toggle_io(PORTD, 1)
#define read_EN_CLOCK_OUT read_io(PORTD, 1)

/* EN_CLOCK_IN */
#define set_EN_CLOCK_IN clear_io(PORTD, 2)
#define clr_EN_CLOCK_IN set_io(PORTD, 2)
#define tgl_EN_CLOCK_IN toggle_io(PORTD, 2)
#define read_EN_CLOCK_IN read_io(PORTD, 2)

/* LED_REPEATER */
#define set_LED_REPEATER set_io(PORTD, 3)
#define clr_LED_REPEATER clear_io(PORTD, 3)
#define tgl_LED_REPEATER toggle_io(PORTD, 3)
#define read_LED_REPEATER read_io(PORTD, 3)

/* LED_LOCK */
#define set_LED_LOCK set_io(PORTD, 4)
#define clr_LED_LOCK clear_io(PORTD, 4)
#define tgl_LED_LOCK toggle_io(PORTD, 4)
#define read_LED_LOCK read_io(PORTD, 4)

/* LED_STATE */
#define set_LED_STATE set_io(PORTD, 5)
#define clr_LED_STATE clear_io(PORTD, 5)
#define tgl_LED_STATE toggle_io(PORTD, 5)
#define read_LED_STATE read_io(PORTD, 5)


/************************************************************************/
/* Registers' structure                                                 */
/************************************************************************/
typedef struct
{
	uint8_t REG_CONFIG;
	uint8_t REG_DEVICES_CONNECTED;
	uint8_t REG_REPEATER_STATUS;
	uint8_t REG_BATTERY_RATE;
	float REG_BATTERY;
	float REG_BATTERY_TH_LOW;
	float REG_BATTERY_TH_HIGH;
	uint16_t REG_BATTERY_CALIBRATION0;
	uint16_t REG_BATTERY_CALIBRATION1;
	uint32_t REG_TIMER;
	uint8_t REG_TIMER_FREQUENCY;
} AppRegs;

/************************************************************************/
/* Registers' address                                                   */
/************************************************************************/
/* Registers */
#define ADD_REG_CONFIG                      32 // U8     Device's configuration
#define ADD_REG_DEVICES_CONNECTED           33 // U8     Reads if the port has a device connected to (bitmask)
#define ADD_REG_REPEATER_STATUS             34 // U8     Check if device is a repeater or spreading internal timestamp
#define ADD_REG_BATTERY_RATE                35 // U8     Configure how oftne the battery calue is sent to computer
#define ADD_REG_BATTERY                     36 // FLOAT  Reads the current battery charge
#define ADD_REG_BATTERY_TH_LOW              37 // FLOAT  Sets the low threshold from where the battery should start to be charged
#define ADD_REG_BATTERY_TH_HIGH             38 // FLOAT  Sets the high threshold from where the battery stops to be charged
#define ADD_REG_BATTERY_CALIBRATION0        39 // U16    Not used
#define ADD_REG_BATTERY_CALIBRATION1        40 // U16    Not used
#define ADD_REG_TIMER                       41 // U32    Unitary counter that periodically produces a value at frequency defined by TIMER_FREQUENCY
#define ADD_REG_TIMER_FREQUENCY             42 // U8     Frequency to produce subsequent values

/************************************************************************/
/* PWM Generator registers' memory limits                               */
/*                                                                      */
/* DON'T change the APP_REGS_ADD_MIN value !!!                          */
/* DON'T change these names !!!                                         */
/************************************************************************/
/* Memory limits */
#define APP_REGS_ADD_MIN                    0x20
#define APP_REGS_ADD_MAX                    0x2A
#define APP_NBYTES_OF_REG_BANK              25

/************************************************************************/
/* Registers' bits                                                      */
/************************************************************************/
#define B_START_BATTERY_CYCLE              (1<<0)       // Starts battery cycle to extend batteries life
#define B_START_DISCHARGE                  (1<<1)       // Starts to discharge right away
#define B_START_CHARGE                     (1<<2)       // Starts to charge right away
#define B_STOPS_ANY                        (1<<3)       // Stop any control of the battery and get back to normal function
#define B_PORT0                            (1<<0)       // 
#define B_PORT1                            (1<<1)       // 
#define B_PORT2                            (1<<2)       // 
#define B_PORT3                            (1<<3)       // 
#define B_PORT4                            (1<<4)       // 
#define B_PORT5                            (1<<5)       // 
#define B_REPEATER                         (1<<0)       // Device is a repeater
#define GM_BATTERY_RATE                    3            // Configures the rate at which the battery charge is sent
#define MSK_EACH_60SECONDS                 0            // Sent each minute
#define MSK_EACH_10SECONDS                 1            // Sent each 10 second
#define MSK_EACH_SECOND                    2            // Sent each second
#define MSK_NEVER                          3            // Not sent
#define GM_TIMER_FREQUENCY                 7            // Configures the rate at which the counter is sent
#define MSK_TIMER_OFF                      0            // Timer is off
#define MSK_TIMER_50HZ                     1            // Counter sent at 50 Hz
#define MSK_TIMER_100HZ                    2            // Counter sent at 100 Hz
#define MSK_TIMER_200HZ                    3            // Counter sent at 200 Hz
#define MSK_TIMER_500HZ                    4            // Counter sent at 500 Hz
#define MSK_TIMER_1000HZ                   5            // Counter sent at 1000 Hz

#endif /* _APP_REGS_H_ */

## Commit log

2021-04-25 Added first firmware files.
    [registers.xls]
2021-04-25 Added an extra 100uF capacitor to +5_USB.
    [harp timestamp generator Gen3 BOM.xlsx, harp timestamp generator Gen3.brd, harp timestamp generator Gen3.sch]
2021-04-25 Added proper filtering to RESET line.
    [harp timestamp generator Gen3 BOM.xlsx, harp timestamp generator Gen3.brd, harp timestamp generator Gen3.sch]
2021-04-28 Corrected the discharge circuit.
    [harp timestamp generator Gen3 BOM.xlsx, harp timestamp generator Gen3.brd, harp timestamp generator Gen3.sch, registers.xls]
2021-05-03 Added replacements.
    [harp timestamp generator Gen3 BOM.xlsx]
2021-05-04 Decreased discharge current by ~60 mA to ~175 mA in average.
    [harp timestamp generator Gen3 BOM.xlsx, harp timestamp generator Gen3.brd, harp timestamp generator Gen3.sch]
2021-05-05 Added ability to initiate battery cycle using the external button.
    [registers.xls]
2022-03-30 Removed LOCK from configuration.
    [registers.xls]
2022-03-30 Removed POWER_GOOD and wake up from buttons' interrupts.
2022-05-04 Changed battery connection to a new location and added an ON/OFF button.
    [copper_bottom_l4.gbr, copper_inner_l2.gbr, copper_inner_l3.gbr, copper_top_l1.gbr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]
2022-05-04 Updated BOM and added front and rear panels.
    [copper_bottom.gbr, copper_top.gbr, gerber_job.gbrjob, harp timestamp generator Gen3 BOM.xlsx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]
2022-05-23 Updated front panel to reflect the right device version.
    [harp timestamp generator Gen3 front panel.brd, silkscreen_top.gbr]
2022-09-22 Added device's photos.
2022-10-05 Added a new power switcher.
    [copper_bottom_l4.gbr, copper_inner_l2.gbr, copper_inner_l3.gbr, copper_top_l1.gbr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]
2022-10-05 Corrected bad battery gauge reader.
    When unplugging and plugging the battery on the fly, the reset of the state machine was not working correctly.
2022-11-17 Minor changes.
    [harp timestamp generator Gen3 BOM.xlsx]
2023-03-28 Add resized device shots and update license
2023-03-28 Refactor repository structure
    [copper_bottom.gbr, copper_bottom_l4.gbr, copper_inner_l2.gbr, copper_inner_l3.gbr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]
2023-03-28 Add prototype device schema and interface
2023-04-03 Corrected files for porduction.
    [gerber_job.gbrjob, harp timestamp generator Gen3 BOM.xlsx, harp timestamp generator Gen3_PnP_TOP.xlsx]
2023-05-09 Replaced Q5 with a correct size component.
    [harp timestamp generator Gen3 BOM.xlsx]
2023-05-18 Fixed the stop command to charge/discharge of the battery
2023-08-14 Update PCB image asset
2024-04-29 Created new registers.
    [registers.xls]
2024-05-30 Fixed #7
    [registers.xls]
2024-05-30 Clean up device.yml
2024-11-09 Update package metadata to embed device metadata
2024-11-10 Favor harp-tech as source of device schema
